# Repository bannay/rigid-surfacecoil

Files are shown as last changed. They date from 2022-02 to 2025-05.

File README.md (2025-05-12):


<!-- PROJECT LOGO -->
<br />
<div align="center">
  <a href="https://github.com/bannay/rigid-surfacecoil">
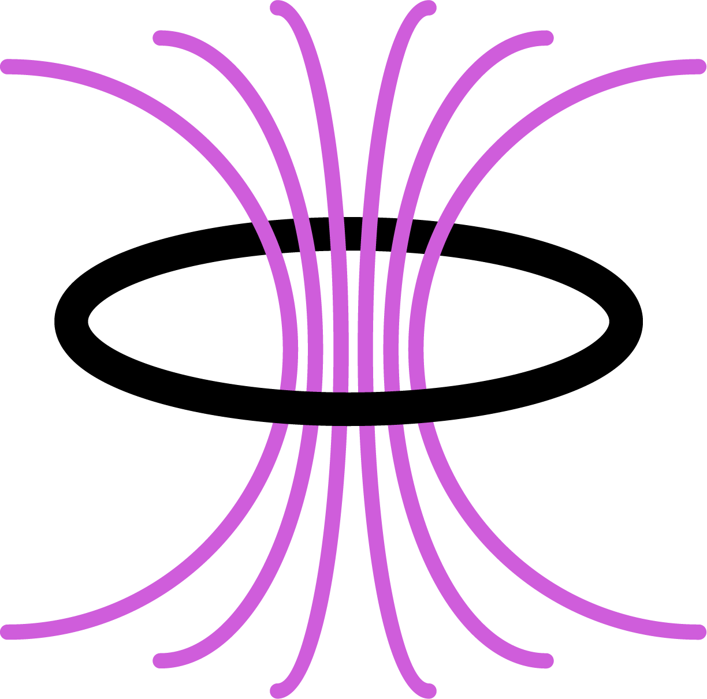
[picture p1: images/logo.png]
    
  </a>
<br>

<h3 align="center">Rigid Ø20 cm MRI surface RF coil</h3>
</div>

<!-- ABOUT THE PROJECT -->
## **About the project**
 Design and construction of a rigid Ø20 cm surface coil using single layer FR-4. Coil geometry and segmentation are optimized to minimize E-field and reduce PCB manufacturing cost. 

### Designed and simulated with
* [KiCAD 6.02]
* [CST Microwave Studio (EM simulator)]
***

<!-- METHOD -->
## **Design**

<!-- CRITERIA -->
### **Criteria**
* Rigid coil  
* 20 cm diameter  
* Frequency and matching tunable  
* Transmit/receive  

<!-- SEGMENTATION & TUNING -->
### **Coil Segmentation and Tuning**

The coil is intended for use on patients and biological samples with an average relative dielectric constant:

$$
\varepsilon_r = 78
$$

If the coil is used for $^1$H detection at 3 Tesla, the Larmor frequency is:

$$
f_0 = 128.57\ \text{MHz}
$$

This corresponds to a wavelength within the sample or patient of:

$$
\lambda_s = \frac{c}{\sqrt{\varepsilon_r} \cdot f_0} = 26.4\ \text{cm}
$$

A rule of thumb stipulates that the contiguous conductor length of the coil should satisfy:

$$
\frac{\lambda_s}{20} < l < \frac{\lambda_s}{10}
$$

which translates to:

$$
1.32\ \text{cm} < l < 2.64\ \text{cm}
$$

In this example, the coils are intended for $^{13}$C, which has a gyromagnetic ratio approximately four times lower than $^1$H. Thus, at 3 Tesla, the Larmor frequency becomes:

$$
f_0 = 32.15\ \text{MHz}
$$

Applying the same rule of thumb, the maximum conductor length becomes:

$$
5.28\ \text{cm} < l < 10.56\ \text{cm}
$$

The total conductor length is:

$$
l = 2\pi r = 68.83\ \text{cm}
$$

This results in a simulated coil inductance of:

$$
L = 575\ \text{nH}
$$

Given the low resonant frequency, 6 segments were selected:

$$
l_{\text{segment}} \approx 11.47\ \text{cm}
$$

This maintains reasonable tuning capacitor values. Accounting for conductor gaps to solder capacitors, this segmentation adheres to the rule of thumb.

The required lumped capacitance to achieve resonance is:

$$
C = \frac{1}{4\pi^2 f^2 L} = 42.6\ \text{pF}
$$

Given six segments, the total distributed capacitance becomes:

$$
C' = 42.6 \times 6 = 255\ \text{pF}
$$

---

### **Matching**

The ideal matching capacitance has been determined via simulation to be:

$$
C_{\text{match}} = 22\ \text{pF}
$$

This value was verified experimentally (using a human thigh to load the coil). For an unloaded coil, matching capacitance can also be analytically approximated based on the coil's lumped capacitance and DC ohmic resistance.

<p align="right">(<a href="#top">back to top</a>)</p>

***

<!-- CONSTRUCTION & FABRICATION -->
## Construction & Fabrication

<!-- BILL OF MATERIALS -->

### **Bill of materials**

* Capacitors were ceramic non-magnetic, purchased from Knowles Syfer and rated to at least 2kV WVDC. 
* Trimmer capacitors for variable tuning and matching were purchased from Knowles Voltronics (V9000).
* 24 x M5 x 8 mm nylon screws.
* 24 x M5 nylon nuts.
* 24 x M5 washers.

<!-- PCB FABRICATION -->
### **PCB fabrication**

The coil has been designed in CST microwave stuido and exported to KiCAD PCB editor (KiCAD and Gerber files available). The coil is made of 6 x 3 PCB pieces: 
* '1-seg' PCB consists of an arched PCB hosting a single 5 mm thick trace. 
* 'Brace' PCB is an empty FR-4 board which aligns between (under) two neighboring '1-seg' PCBs and mechanically couples them together.
* 'Coupler' PCB has castellated edges and is soldered between (above) two neighboring '1-seg' PCBs to host tuning/matching capacitors and a coaxial cable.

Provided the surface coil is segmented into smaller boards - then fabrication is relatively affordable arriving to 144.45 USD for 12 coils (~12 USD per coil).

The PCBs 1-seg and Brace are mechanically fastened together using nylon screws.

Note, not all couplers need to be solder on if less than 6 segments are required.  

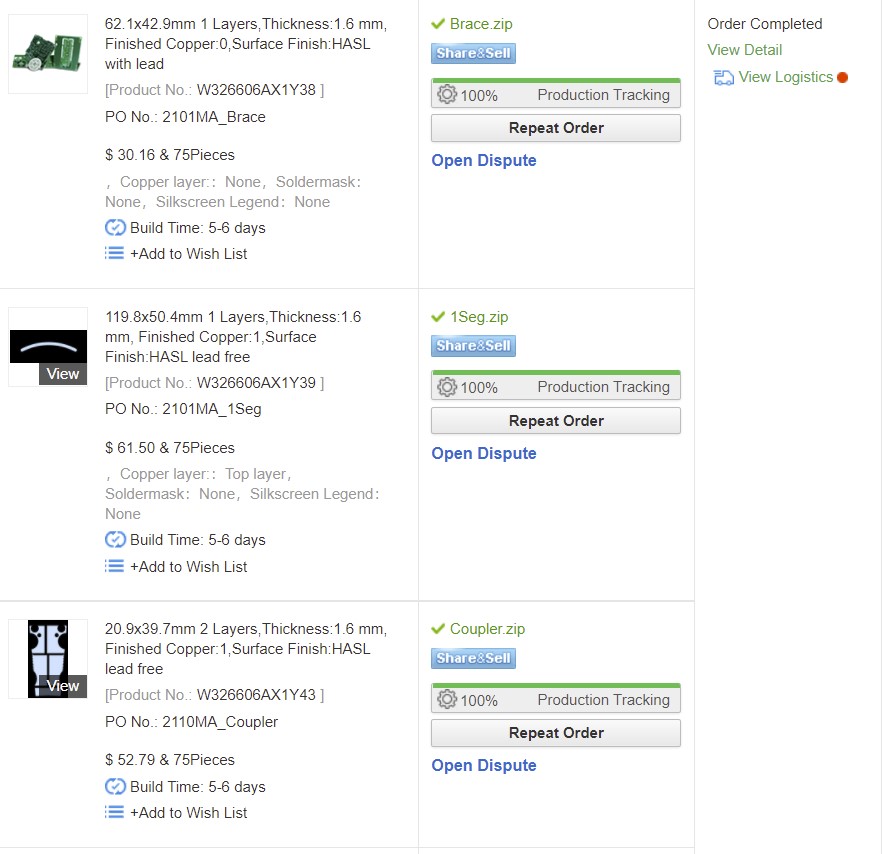
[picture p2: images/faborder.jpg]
faborder

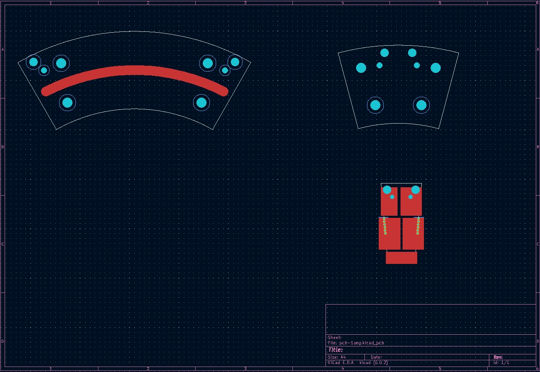
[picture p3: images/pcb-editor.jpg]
pcb-editor


<p align="right">(<a href="#top">back to top</a>)</p>

***

<!-- Images -->
## Images
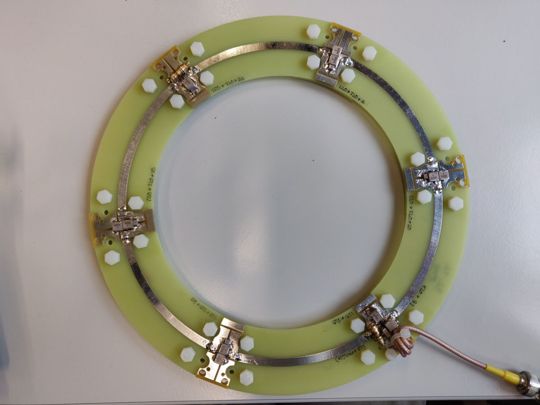
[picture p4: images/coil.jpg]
coil

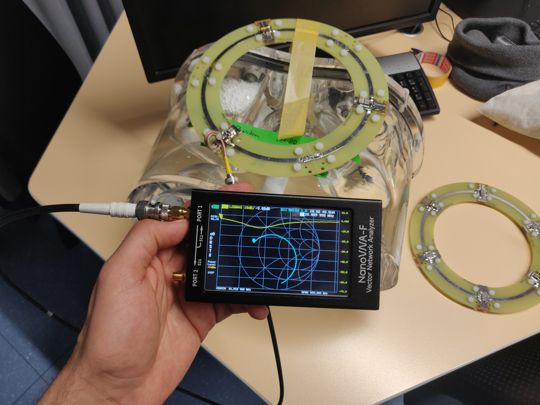
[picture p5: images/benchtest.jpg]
benchtest

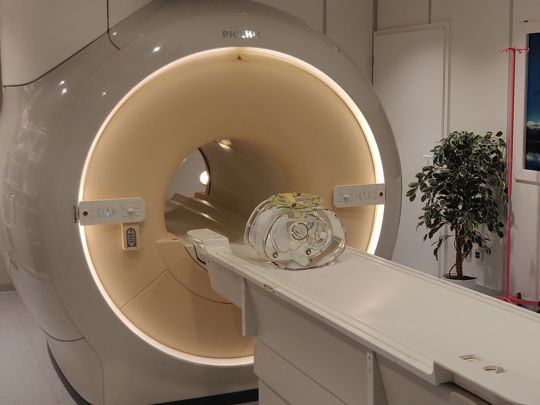
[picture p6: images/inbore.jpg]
inbore

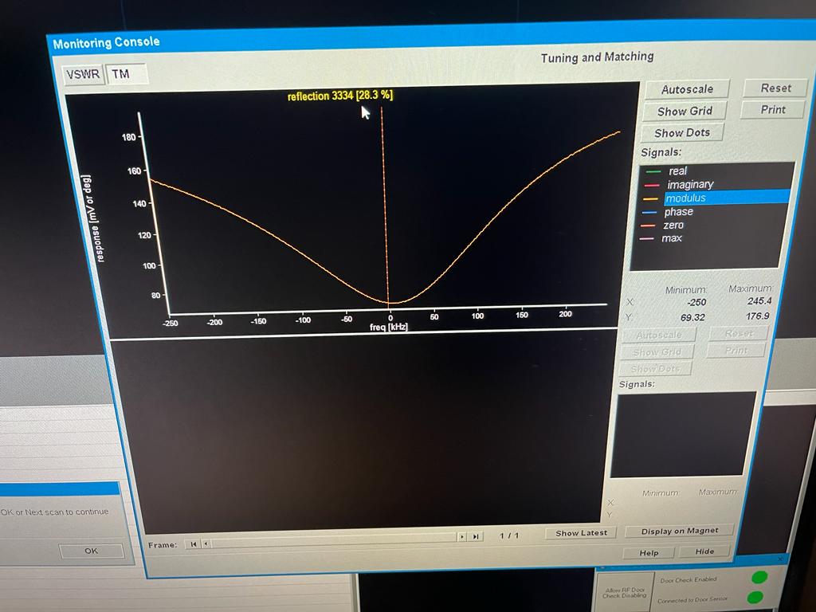
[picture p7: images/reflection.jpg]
reflection


<p align="right">(<a href="#top">back to top</a>)</p>

***

<!-- LICENSE -->
## License

Distributed under the MIT License. See `LICENSE.txt` for more information.

<!-- CONTACT -->
## Contact

Mohammed M. Albannay - [@Bannay](https://twitter.com/bannay) - bannay@gmail.com

Project Link: [https://github.com/bannay/rigid-surfacecoil](https://github.com/bannay/rigid-surfacecoil)

<!-- ACKNOWLEDGMENTS -->
## Acknowledgments

* [Readme template](https://github.com/othneildrew/Best-README-Template)

<p align="right">(<a href="#top">back to top</a>)</p>

***
